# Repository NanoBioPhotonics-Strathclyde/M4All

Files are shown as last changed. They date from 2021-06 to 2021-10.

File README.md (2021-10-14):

# M4All: MultiModal Modular Microscopy for All


M4All is a modular 3D printable microscopy system which allows users to design setups for different imaging modalities (can also be used for non-imaging optical systems). The project is led by Gemma Cairns as part of her PhD in the NanoBioPhotonics group at the University of Strathclyde. Other significant contributers from the group are Brian Patton and past member Stephen Grant.

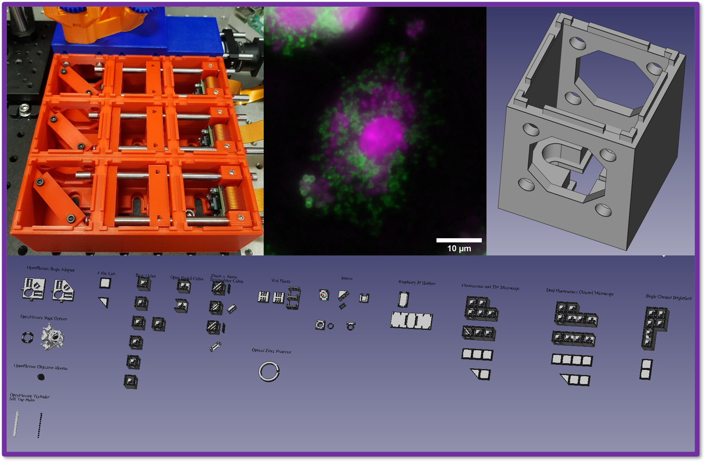
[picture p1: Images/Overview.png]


There are multiple approaches for open microscopy hardware, for example see the project list at https://github.com/HohlbeinLab/OpenMicroscopy, and we recommend trying a few and choosing a project based on what your aims are. When designing this system we approached it from the view point of requiring light tight and stable setups which would allow us to implement and test cutting edge microscopy techniques on a budget. As such M4All is best suited to those with prior microscopy experience or those working with people with similar optical experience. We are confident that M4All systems allow us to generate publication quality images and results.

M4All is based on modular cubes which include 6mm rod holes compatible with standard 30mm cage system optomechanics (multiple manufacturers make compatible components). There are various challenges when it comes to 3D printing, especially when the aim is to create accurate structures for imaging devices. There are often discrepancies between different 3D printers and their printing tolerances. Even small defects in printed parts can be enough to cause problems when trying to join different parts together, which in turn can lead to alignment and stability problems in 3D printed imaging systems. To try and address this problem, our approach is to provide a package of modular cube design files which can be joined together to create larger parts prior to printing to improve stability. By printing larger parts, or ideally the microscope as one single body if printing dimensions allow, this reduces the number of errors that can build up when printing individual modular cubes, although at the expense of decreased flexibility post printing. Note that this approach should not change the total printing time.

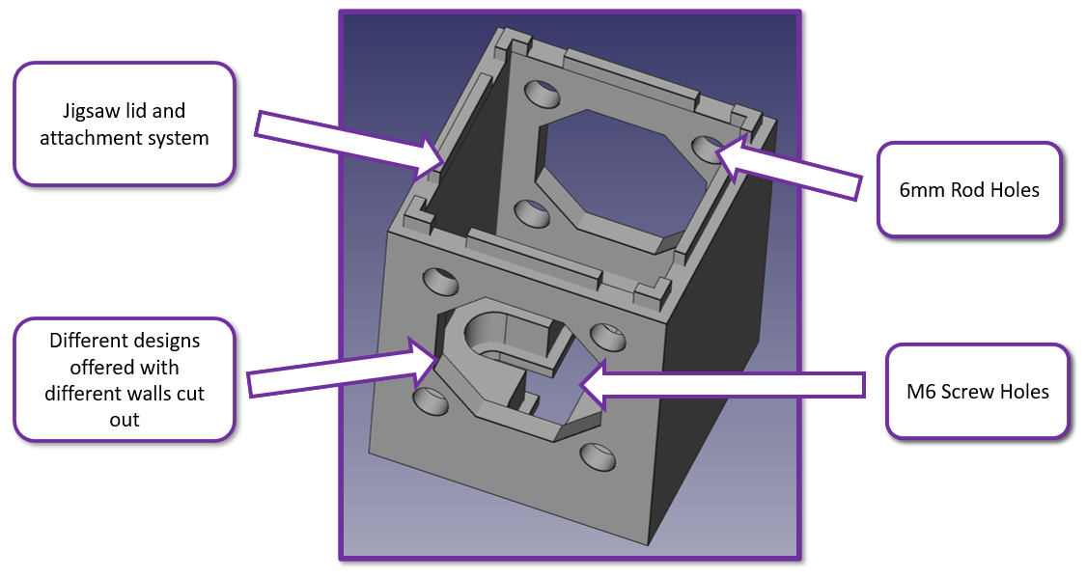
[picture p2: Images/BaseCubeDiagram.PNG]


You can see the base cube design above with the cage system highlighted. The cubes also have M6 screw holes on the bottom to allow securing parts onto an optical bench or other surface and to hold larger parts together in the system. We have included a jigsaw system on the top of the cubes as well to attach corresponding light tight lids or attachments for other parts, such as one we have designed to allow the OpenFlexure Microscope (https://openflexure.org/projects/microscope/) to be compatible with our system. On the topic of keeping imaging systems light tight, we have also provided an array of base cube designs with different walls cut out and including the cage system so that users can design their microscope with the outer walls closed. For alternatives to commercial optomechanics we have also provided designs for 3D printed parts compatible with this system to hold various different optics, such as lenses, mirrors, beamsplitters, dichroics and raspberry pi cameras.

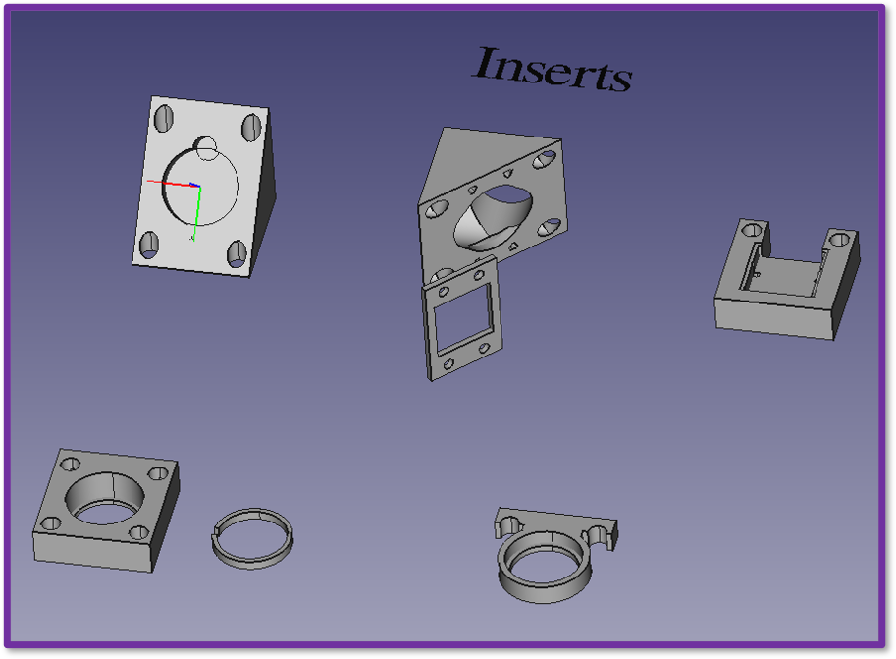
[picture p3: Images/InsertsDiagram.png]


To address the differences in printing tolerances between different 3D printers, we also provide test pieces which users can print to optimise both design dimensions and printer settings. For example the two test pieces shown below allow you to determine which radius to set the 6mm rod holes as in the CAD files so that they aren't too large or small when printing the cubes and inserts. Tolerances also vary for printing in either the xy or z planes and so this is why there are two test piece orientations.

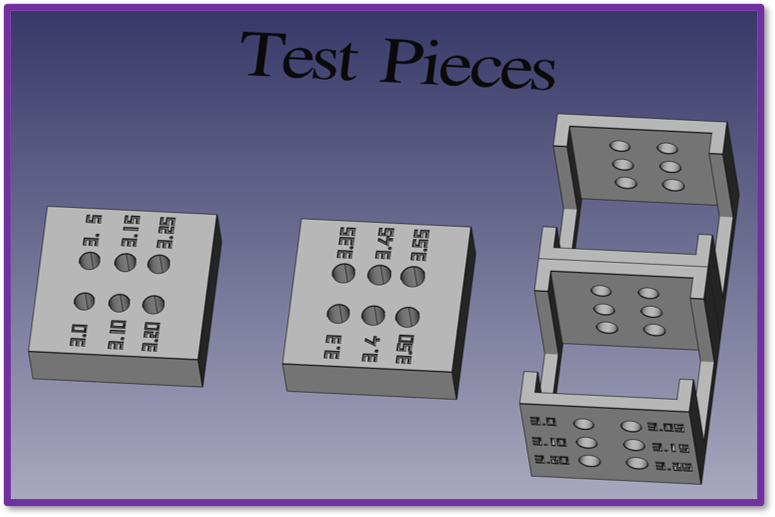
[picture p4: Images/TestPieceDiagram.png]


## Applications

We have used this system to design and build multiple different microscopes.

The first is a [Single Channel Brightfield Microscope](https://github.com/NanoBioPhotonics-Strathclyde/M4All/blob/main/3D%20Printer%20Design%20Files/Build%20Instructions/SingleChannelBrightfield.md). We recommend new users to our system build one of these first to understand our approach and calibrate their 3D printer for our designs.

The next is a [Fluorescence and TIE Microscope](https://github.com/NanoBioPhotonics-Strathclyde/M4All/blob/main/3D%20Printer%20Design%20Files/Build%20Instructions/FluorescenceandTIEMicroscope.md) which shows the level of complexity that can be successfully implemented with our designs:

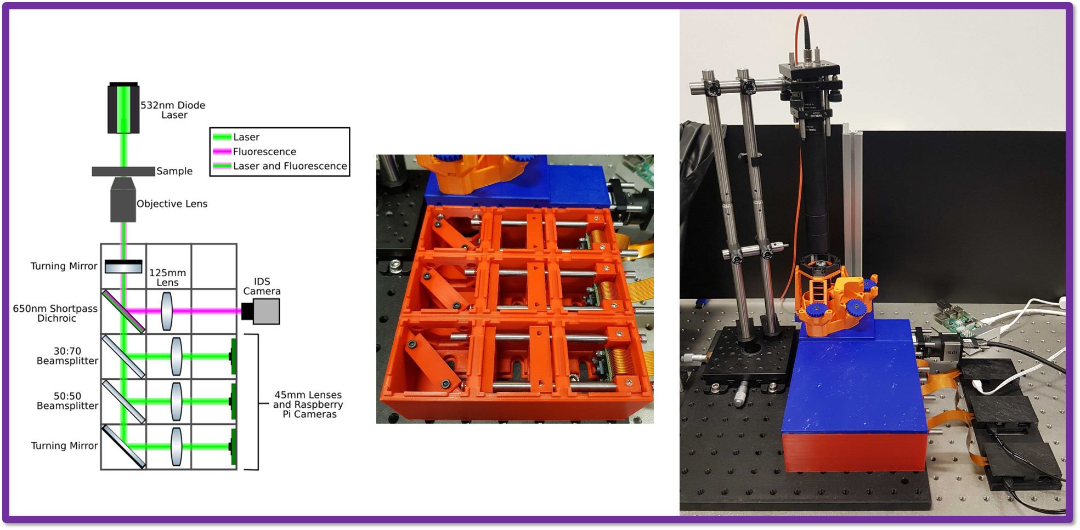
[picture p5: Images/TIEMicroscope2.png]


The third is a [Dual Fluorescence Channel Microscope](https://github.com/NanoBioPhotonics-Strathclyde/M4All/blob/main/3D%20Printer%20Design%20Files/Build%20Instructions/DualFluorescenceMicroscope.md). This microscope takes fluorescence images with the latest Raspberry Pi HQ cameras.

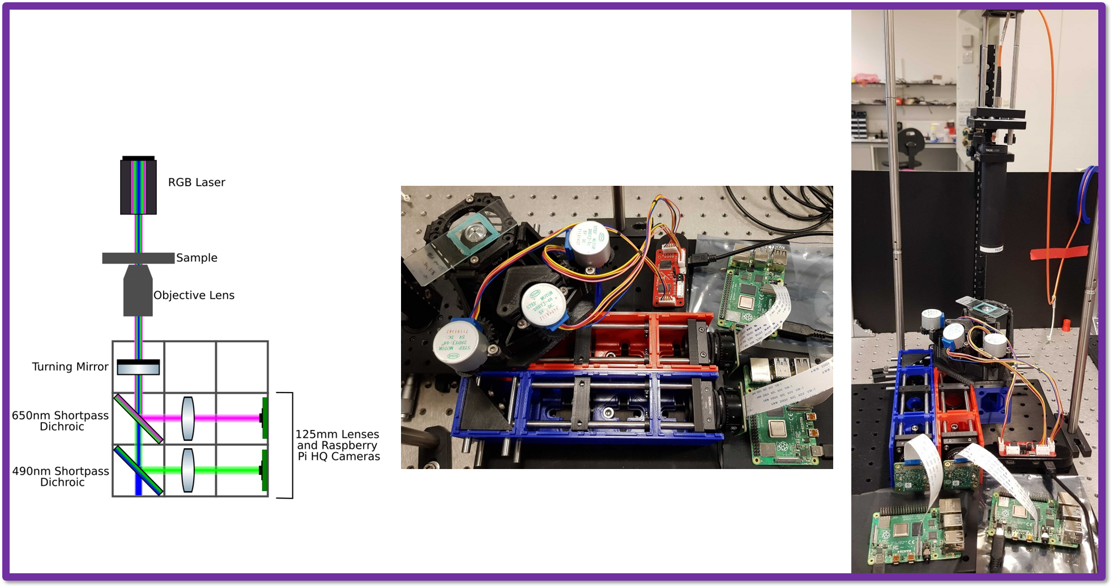
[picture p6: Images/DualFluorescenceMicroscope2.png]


We have successfully used this microscope in a research project to acquire images of bacteria and mitochondria in human monocyte derived macrophages:

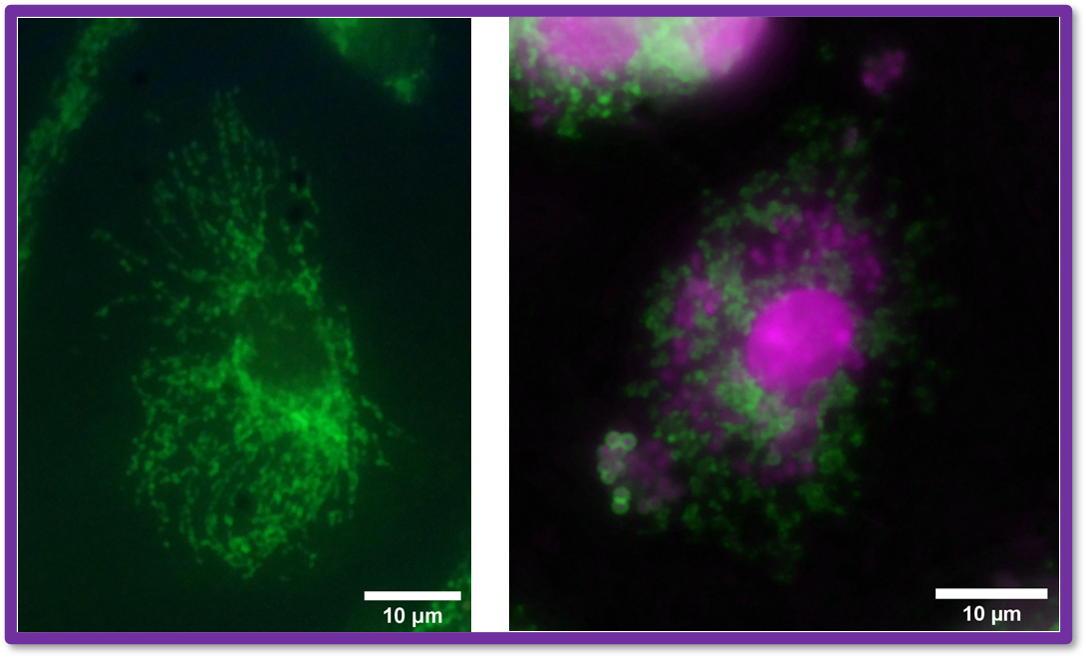
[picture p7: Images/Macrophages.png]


## Design Files and Build Instructions

All of our designs are produced using the open source CAD software FreeCAD (https://www.freecadweb.org/).

Note: We used FreeCAD version 0.18 which can be found here https://github.com/FreeCAD/FreeCAD/releases if there are any compatibility issues with newer releases.

For FreeCAD and STL design files please see the [3D Printer Design Files](https://github.com/NanoBioPhotonics-Strathclyde/M4All/tree/main/3D%20Printer%20Design%20Files) folder.
This section also includes build instructions.

Note: We have also included modified designs from the OpenFlexure project (https://openflexure.org/projects/microscope/). Original designs and modifications are detailed in the design folders in accordance with the CERN Open Hardware Licence.

## Control Software

For microscope control software please see [Control Software](https://github.com/NanoBioPhotonics-Strathclyde/M4All/tree/main/Control%20Software). 

Note: We are not software engineers and so these options may not necessarily be optimal but for now they let us acquire the data that we need for our research.

## Multi Channel Alignment and Calibration Tools

Coming soon...

## Licence

Our hardware designs are licenced under the CERN Open Hardware Licence Version 2 (CERN-OHL-S).

Our software is licenced under the GNU General Public License v3.0.

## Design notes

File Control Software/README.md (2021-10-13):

# Control Software

There are a couple of different options that we use for controlling our 3D printed microscopes, depending on the system. Note: We are not software engineers and so these options may not necessarily be optimal but for now they let us acquire the data that we need for our research.

## Stepper Motor Control

To control the stepper motors connected to the axis actuators on the OpenFlexure stage we use a PiStep2 Quad Stepper Motor Control Board for Raspberry Pi (https://4tronix.co.uk/blog/?p=1309). This is a hat for the Raspberry Pi GPIO pins and allows up to four stepper motors to directly connect to it. We have tested this with a Pi Zero W, Pi 3 Model B+ and Pi 4 Model B. To control the PiStep2 and the motors we have created a simple Python GUI based on Qt and PyQt5. The code can be found in [StepperMotorGUI](https://github.com/NanoBioPhotonics-Strathclyde/M4All/tree/main/Control%20Software/StepperMotorGUI). To run the GUI, open and run the file start.py on your Raspberry Pi. The GUI should look like this:

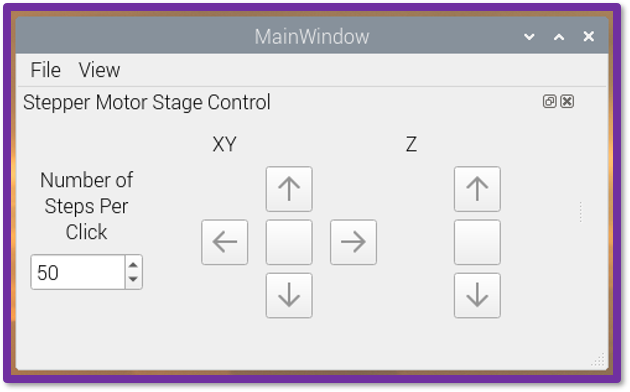
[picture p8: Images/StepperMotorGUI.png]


The default value for the number of steps per click is 50. Altering this will let you control how far the stepper motor turns when you click on the arrow buttons for each axis.

Note: you will need to set up the Pi as outlined [here](https://github.com/NanoBioPhotonics-Strathclyde/M4All/blob/main/Control%20Software/SingleChannelPiSetup.md) for the code to run.

## Single Channel Brightfield Microscope

To see the details of this microscope please go to [Single Channel Brightfield Microscope](https://github.com/NanoBioPhotonics-Strathclyde/M4All/blob/main/3D%20Printer%20Design%20Files/Build%20Instructions/SingleChannelBrightfield.md).

The core components of this microscope are a basic LED for illumination, an OpenFlexure stage, a 60x finite conjugate objective and a Raspberry Pi Camera Module v2. We have created a simple GUI to control this microscope and take timelapse images on the Raspberry Pi camera. The code for this software can be found in [StepperMotorandLEDGUI](https://github.com/NanoBioPhotonics-Strathclyde/M4All/tree/main/Control%20Software/StepperMotorandLEDGUI). Again, to run the GUI, open and run the file start.py on your RaspberryPi. The GUI should look like this:

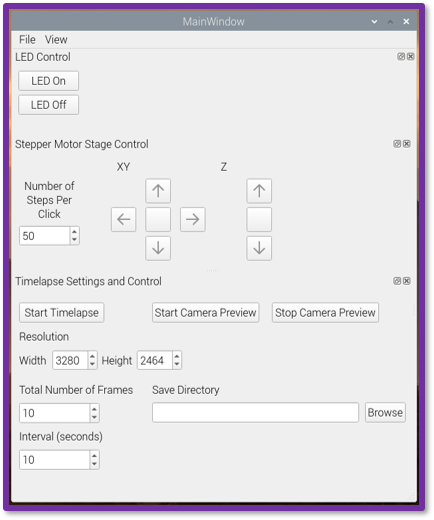
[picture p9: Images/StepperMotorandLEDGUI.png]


This includes control to switch an LED, which is connected to the PiStep2 hat, on and off. Again, please follow the link to the microscope details above for how to connect this. The same stepper motor control as above is included as well as a section to control the Raspberry Pi Camera. A camera preview can be initiated which allows you to view a live feed whilst controlling the stepper motors. When happy with the position, the camera preview must be stopped before starting a timelapse. To start the timelapse, set the desired camera resolution, the total number of frames required and the interval between each frame. Then select a save directory and click start timelapse. When the timelapse is running a camera preview will also be shown.

Note: you will need to set up the Pi as outlined [here](https://github.com/NanoBioPhotonics-Strathclyde/M4All/blob/main/Control%20Software/SingleChannelPiSetup.md) for the code to run.

## Multi Channel Microscopes

Multi channel microscopes using multiple Raspberry Pi cameras, such as our [Fluorescence and TIE Microscope](https://github.com/NanoBioPhotonics-Strathclyde/M4All/blob/main/3D%20Printer%20Design%20Files/Build%20Instructions/FluorescenceandTIEMicroscope.md) and [Fluorescence Channel Microscope](https://github.com/NanoBioPhotonics-Strathclyde/M4All/blob/main/3D%20Printer%20Design%20Files/Build%20Instructions/DualFluorescenceMicroscope.md) require more complex software solutions. This is due to the fact that a Raspberry Pi can only connect to and control a single Raspberry Pi camera module. Because of this, if you want to use multiple Pi cameras, you need to use and control multiple Pi's.

Our current method of choice is to use a Raspberry Pi 4 Model B 8gb as a client (controller) Pi. We then connect each camera and the stepper motor hat to separate Pi's (servers) as can be seen in the microscope links above. We connect the client and server Pi's all to the same network. Instructions for connecting to a network can be found here: https://projects.raspberrypi.org/en/projects/raspberry-pi-using/3#:~:text=If%20you%20want%20to%20connect,connect%20to%20a%20wireless%20network.

To view the camera previews and control the stepper motors we use VNC (Virtual Network Computing) to remote access the server Pi desktops on the client Pi, so that only the client pi needs to be connected to a monitor, mouse and keyboard. For example in the image below you can see one remote desktop on the client Pi has one of the camera previews and the other has the stepper motor control GUI. You can open multiple remote desktops at once and so can have all the camera previews open. If using v2 camera modules, Pi Zero Ws work for the server Pi's, if using HQ camera modules we recommend using at least Pi 3B+ or optimally Pi 4 8GB. 

To set these Raspberry Pi's up please follow the instructions [here](https://github.com/NanoBioPhotonics-Strathclyde/M4All/blob/main/Control%20Software/MultiChannelSetup.md).

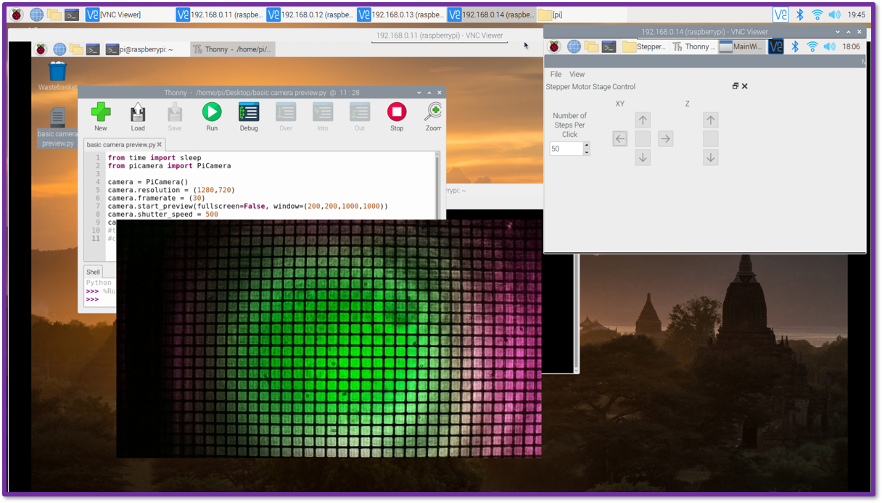
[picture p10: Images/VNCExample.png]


Using the remote desktop approach above, you can capture images from individual cameras using Raspicam (https://www.raspberrypi.com/documentation/accessories/camera.html#raspicam-commands) or Picamera (https://picamera.readthedocs.io/en/release-1.13/). This will save images to the individual pi's that the cameras are connected to and you cannot take images simultaneously.

If you would like to capture images "simultaneously" and save the images to the client Pi then the solution we have been using is the Compound Pi project (https://compoundpi.readthedocs.io/en/release-0.4/). Because the Raspberry Pi cameras use a rolling shutter to capture images there is a limitation on how simultaneous capture can actually be along with any possible network delay using the Compound Pi method. However we have achieved simultaneous capture within one tenth of a second using this method (may be more accurate than this but our stopclock at the time had limited precision). Instructions for setting up the Pi's to use Compound Pi can be found [here](https://github.com/NanoBioPhotonics-Strathclyde/M4All/blob/main/Control%20Software/MultiChannelSimultaneousSetup.md).

Another option separate from using VNC and Compound Pi is to use motionEyeOS (https://github.com/ccrisan/motioneyeos/wiki), however there are limitations on camera resolution and what camera settings you can control.

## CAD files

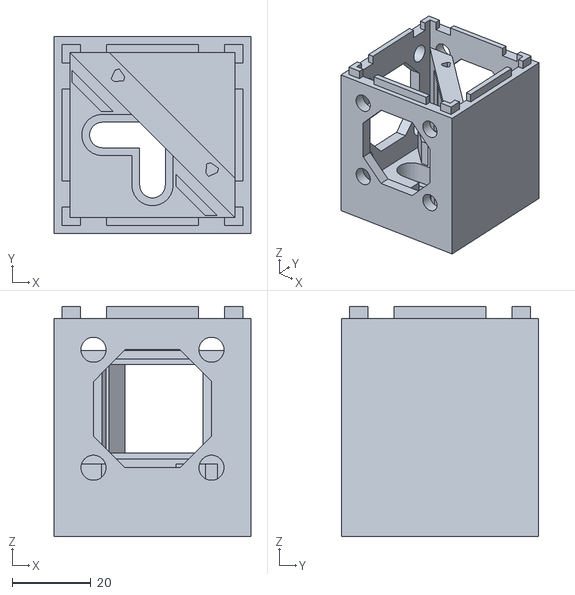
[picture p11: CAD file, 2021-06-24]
3D Printer Design Files/STL Files/25mm x 36mm Beamsplitter Cubes/Beamsplitter Cube 001/Beamsplitter Cube 001.stl
50.0 x 50.0 x 58.5

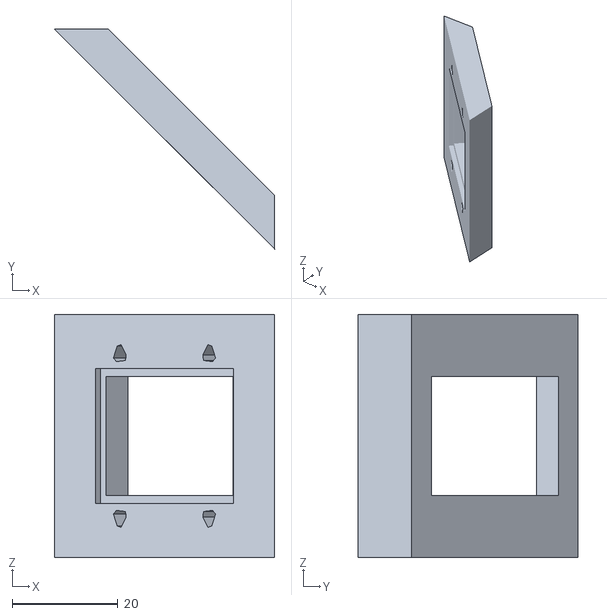
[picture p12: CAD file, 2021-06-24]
3D Printer Design Files/STL Files/25mm x 36mm Beamsplitter Cubes/Beamsplitter Cube 002/Plate Holder.stl
41.7 x 41.7 x 46.0

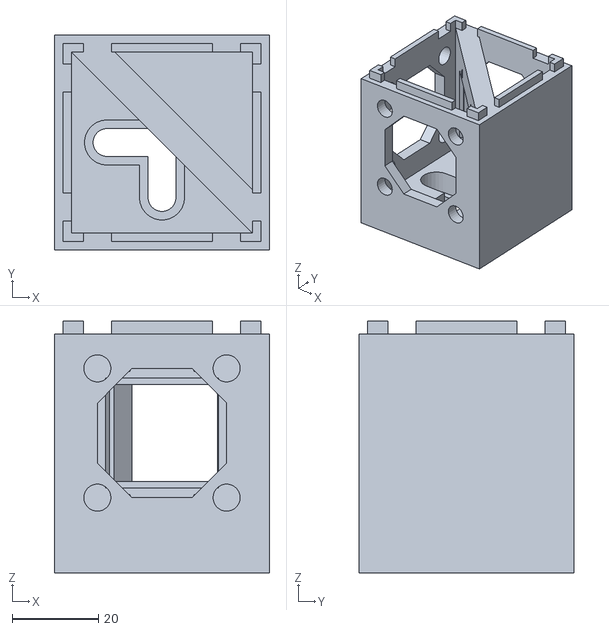
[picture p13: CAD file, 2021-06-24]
3D Printer Design Files/STL Files/25mm x 36mm Beamsplitter Cubes/Beamsplitter Cube/Beamsplitter Cube.stl
50.0 x 50.0 x 58.5

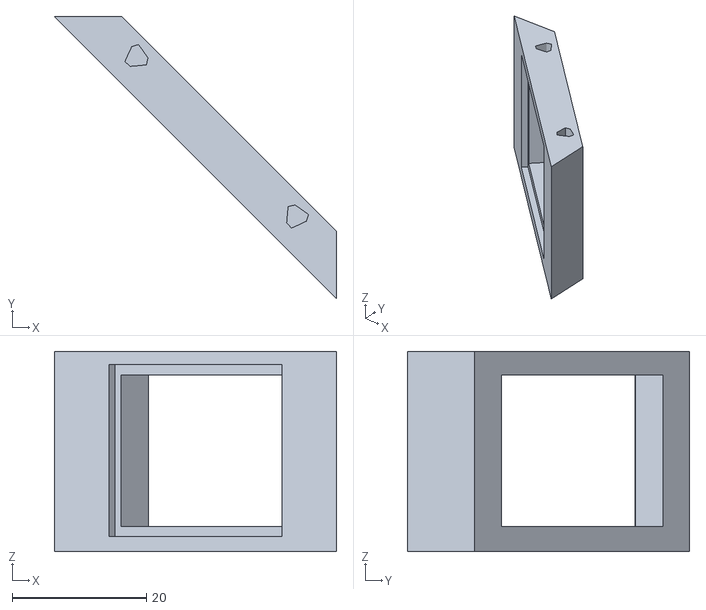
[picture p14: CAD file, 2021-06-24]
3D Printer Design Files/STL Files/25mm x 36mm Beamsplitter Cubes/Plate Holder.stl
42.0 x 42.0 x 29.9

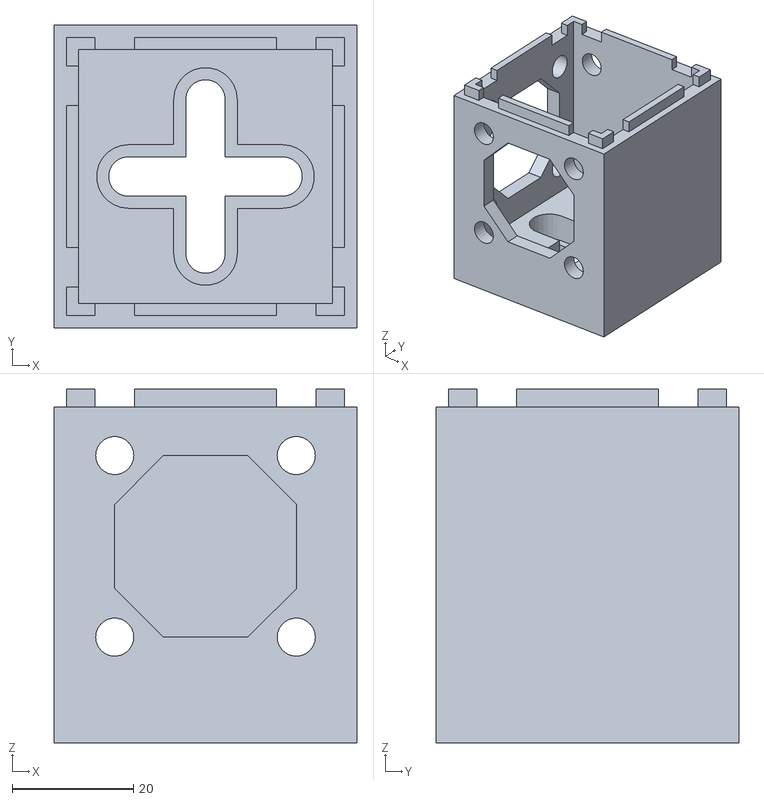
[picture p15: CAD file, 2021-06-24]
3D Printer Design Files/STL Files/Basic Cubes/Cube 2 Sides Cut Out Adjacent.stl
50.0 x 50.0 x 58.5

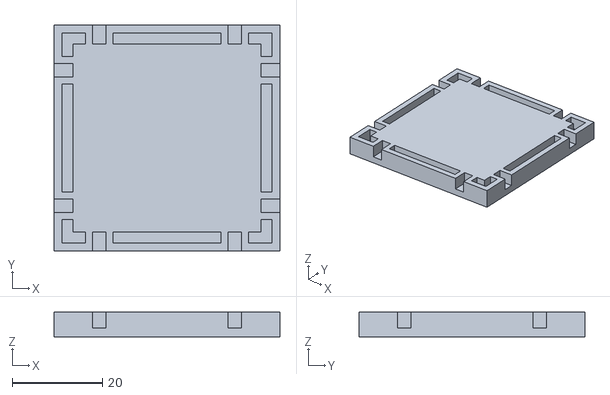
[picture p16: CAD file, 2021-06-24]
3D Printer Design Files/STL Files/Cube Lids/1x1 Cube Lid.stl
50.0 x 50.0 x 5.50

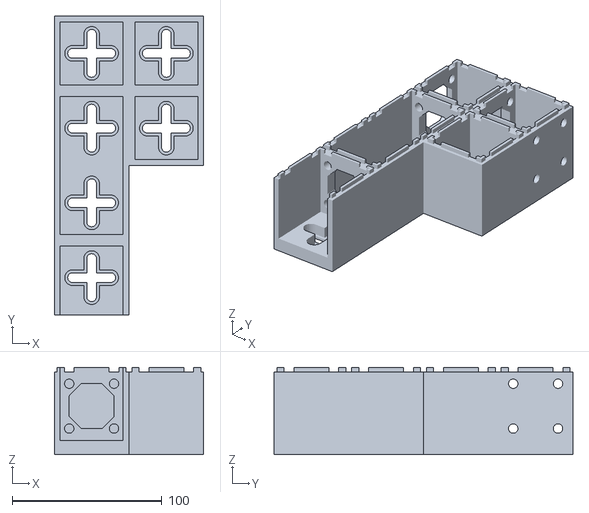
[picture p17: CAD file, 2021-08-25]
3D Printer Design Files/STL Files/Dual Fluorescence Channel Microscope/Channel 1.stl
100.0 x 200.0 x 58.5

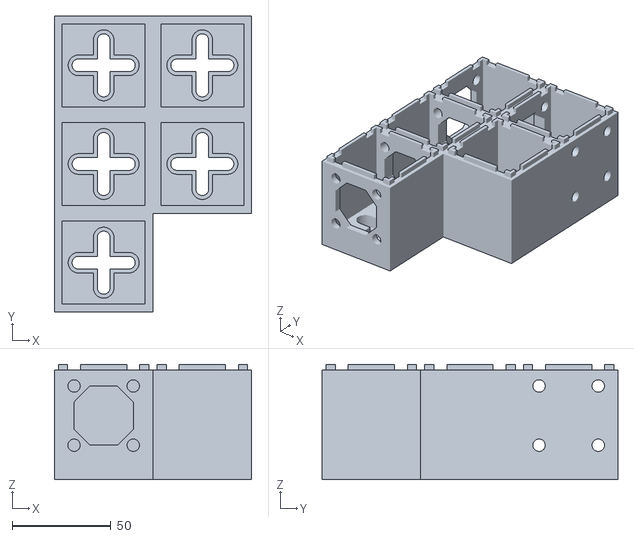
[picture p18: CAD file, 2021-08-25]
3D Printer Design Files/STL Files/Fluorescence and TIE Microscope/Fluorescence Branch.stl
100.0 x 150.0 x 58.5

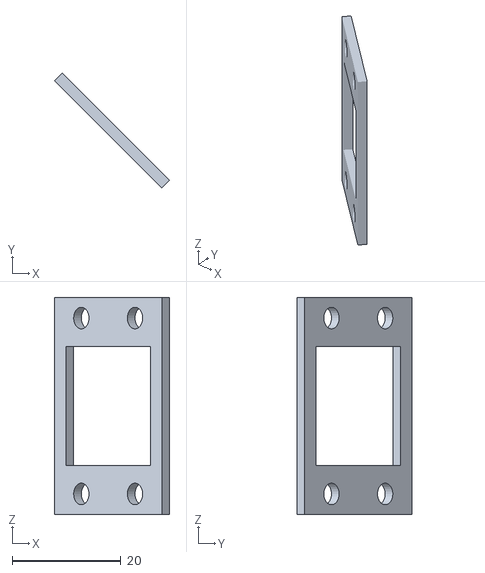
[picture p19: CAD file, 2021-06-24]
3D Printer Design Files/STL Files/Inserts/Dichroic Locker.stl
21.2 x 21.2 x 40.0

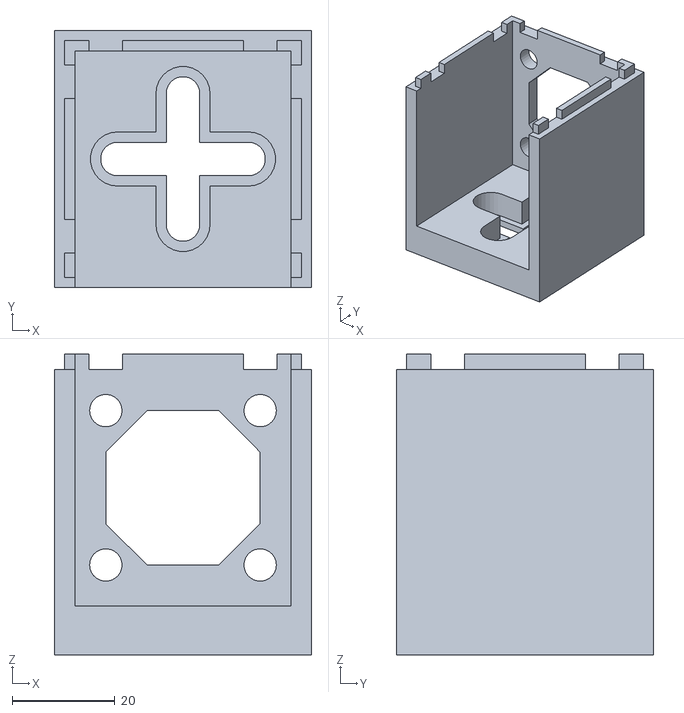
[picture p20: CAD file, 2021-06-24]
3D Printer Design Files/STL Files/Open Ended Cubes/Cube 1 Side Open Ended.stl
50.0 x 50.0 x 58.5

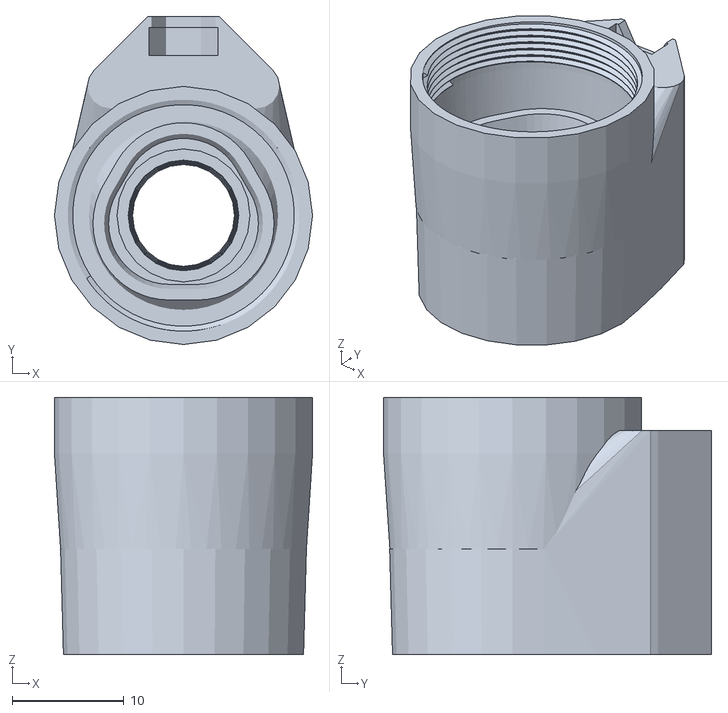
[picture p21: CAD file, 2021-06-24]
3D Printer Design Files/STL Files/OpenFlexure Objective Mount/RMS Objective Mount.stl
23.1 x 29.3 x 23.0

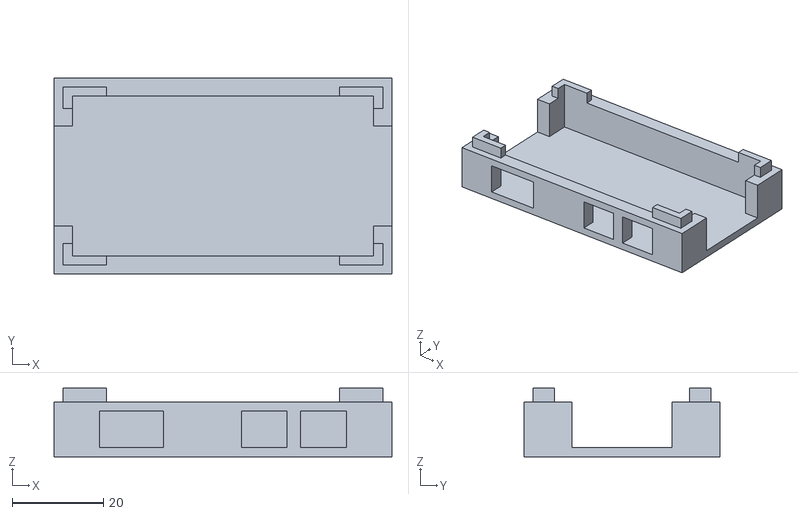
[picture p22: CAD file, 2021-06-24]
3D Printer Design Files/STL Files/Raspberry Pi Holders/Raspberry Pi Zero Case.stl
74.0 x 43.0 x 15.0

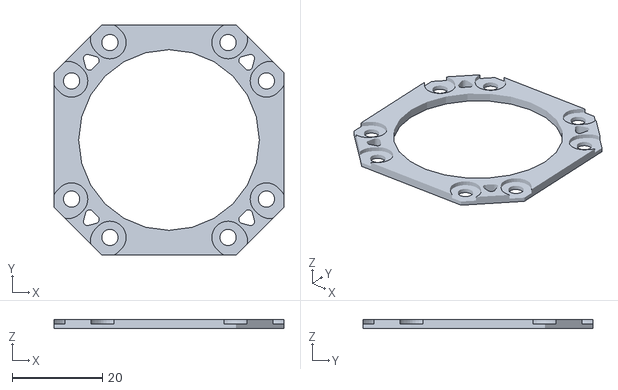
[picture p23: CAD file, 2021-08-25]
3D Printer Design Files/STL Files/Single Channel Brightfield/OpenFlexure Sample Riser Shortened.stl
50.9 x 50.9 x 2.00

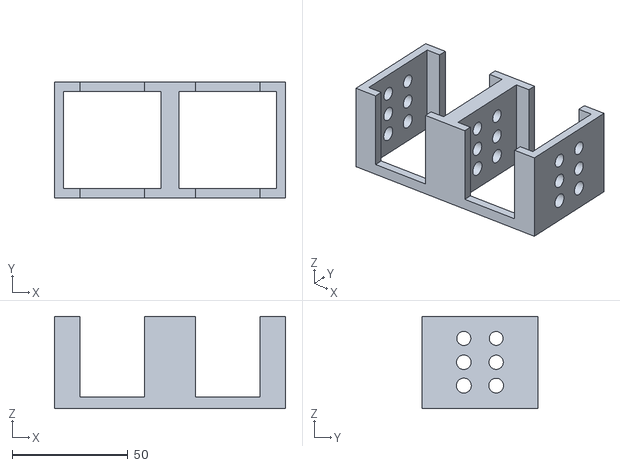
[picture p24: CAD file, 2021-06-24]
3D Printer Design Files/STL Files/Test Pieces/Rod Hole Test Piece Vertical.stl
100.0 x 50.0 x 40.0

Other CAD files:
3D Printer Design Files/STL Files/25mm x 36mm Beamsplitter Cubes/Beamsplitter Cube 002/Beamsplitter Cube 002.stl
3D Printer Design Files/STL Files/25mm x 36mm Beamsplitter Cubes/Beamsplitter Cube/Plate Locker.stl
3D Printer Design Files/STL Files/Basic Cubes/Cube 3 Sides Cut Out.stl
3D Printer Design Files/STL Files/Dual Fluorescence Channel Microscope/OpenFlexure Stage Adapter Corner Cut Out.stl
3D Printer Design Files/STL Files/25mm x 36mm Beamsplitter Cubes/Beamsplitter Cube 002/Plate Locker.stl
3D Printer Design Files/STL Files/Basic Cubes/Cube 0 Sides Cut Out.stl
3D Printer Design Files/STL Files/Basic Cubes/Cube 1 Side Cut Out With Camera Cable Slot.stl
3D Printer Design Files/STL Files/Basic Cubes/Cube 1 Side Cut Out.stl
3D Printer Design Files/STL Files/Basic Cubes/Cube 2 Sides Cut Out.stl
3D Printer Design Files/STL Files/Basic Cubes/Cube 4 Sides Cut Out.stl
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

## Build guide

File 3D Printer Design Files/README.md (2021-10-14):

# Build Instructions

Original FreeCAD design files are in the [FreeCAD Files](https://github.com/NanoBioPhotonics-Strathclyde/M4All/tree/main/3D%20Printer%20Design%20Files/FreeCAD%20Files) folder.

Note: We used FreeCAD version 0.18 which can be found here https://github.com/FreeCAD/FreeCAD/releases if there are any compatibility issues with newer releases.

STL files for 3D printing can be found in the [STL Files](https://github.com/NanoBioPhotonics-Strathclyde/M4All/tree/main/3D%20Printer%20Design%20Files/STL%20Files) folder.

## FreeCAD Instructions

Upon opening the FreeCAD file named "Designs", found [here](https://github.com/NanoBioPhotonics-Strathclyde/M4All/tree/main/3D%20Printer%20Design%20Files/FreeCAD%20Files), you will see that the designs are all grouped into different areas. Below is a brief overview of our design groups with further information found in [Build Instructions](https://github.com/NanoBioPhotonics-Strathclyde/M4All/tree/main/3D%20Printer%20Design%20Files/Build%20Instructions)). Each section in the build instructions has print settings recommended for each part and we also include details of three different microscopes we have built using the M4All system.

Once you have familiarised yourself with our designs we recommend following steps 1 and 2 below to optimise designs/calibrate print settings. We recommend optimising a single cube before printing larger systems. Once happy with this you can either print the parts for one of the three microscopes we describe below (we recommend starting with the single channel brightfield microscope), or you can create your own cube systems using the instructions in step 3 below.

* [**Cubes**](https://github.com/NanoBioPhotonics-Strathclyde/M4All/blob/main/3D%20Printer%20Design%20Files/Build%20Instructions/Cubes.md):
  * **Basic Cubes** are the basic building blocks of the modular system. Included are various cube designs with different numbers of sides cut out for joining together in different orientations for the optical system that the user requires. The cubes have screw holes in the bottom to allow them to be screwed onto an optical table, using M6 screws, for stability and to lock separate parts together. The cubes have 6mm rod holes compatible with 30mm cage system optomechanics.
  * **Open Ended Cubes** are similar to the basic cubes but have entire walls cut out for creating extended cubes where maybe a wall would be at a position where you would like an optical element to be placed. 
  * **25mm x 36mm Beamsplitter Cubes** include three different options for specifically holding 25mm x 36mm plate beamsplitters/dichroics/ mirrors.
  * **Cube Lids** are screwless lids that fix onto the top of the cubes using a jigsaw system to allow a light tight optical setup.
* [**Inserts**](https://github.com/NanoBioPhotonics-Strathclyde/M4All/blob/main/3D%20Printer%20Design%20Files/Build%20Instructions/Inserts.md) includes design files for holding different optical elements using the 30mm cage system. So far these include:
  * a 45 degree 1 inch mirror holder
  * a 1 inch plate dichroic holder with plate to lock dichoic in place.
  * a 1 inch lens holder with retaining ring
  * a Raspberry Pi Camera v2 holder
  * a drop in 1 inch filter holder
* [**Raspberry Pi Holders**](https://github.com/NanoBioPhotonics-Strathclyde/M4All/blob/main/3D%20Printer%20Design%20Files/Build%20Instructions/RaspberryPiHolders.md) includes raspberry pi cases that can be screwed onto an optical table for stability.
* [**OpenFlexure Stage Adapter**](https://github.com/NanoBioPhotonics-Strathclyde/M4All/blob/main/3D%20Printer%20Design%20Files/Build%20Instructions/OpenFlexureStageAdapter.md) is an adapter plate for the OpenFlexure microscope, using the same jigsaw system as the cube lids, to allow the OpenFlexure xyz stage to be used.
* **Test Pieces** allow users to find the best settings and design dimensions for their specific 3D printers before printing full designs.
* [**Single Channel Brightfield Microscope**](https://github.com/NanoBioPhotonics-Strathclyde/M4All/blob/main/3D%20Printer%20Design%20Files/Build%20Instructions/SingleChannelBrightfield.md) includes larger parts recommended to build a simple single channel brightfield microscope. We recommend building one of these first if new to our system in order to understand our approach and calibrate your 3D printer for our designs.
* [**Fluorescence and TIE Microscope**](https://github.com/NanoBioPhotonics-Strathclyde/M4All/blob/main/3D%20Printer%20Design%20Files/Build%20Instructions/FluorescenceandTIEMicroscope.md) includes larger recommended parts made up of the modular cubes for a multimodal microscope setup including fluorescence and computational phase contrast imaging.
* [**Dual Fluorescence Channel Microscope**](https://github.com/NanoBioPhotonics-Strathclyde/M4All/blob/main/3D%20Printer%20Design%20Files/Build%20Instructions/DualFluorescenceMicroscope.md) again includes larger recommended parts for a dual channel fluorescence microscope.

### Step 1: Test Pieces

As the tolerances of different models of 3D printers and different 3D printing materials vary, it is recommended to print the test parts provided [here](https://github.com/NanoBioPhotonics-Strathclyde/M4All/tree/main/3D%20Printer%20Design%20Files/STL%20Files/Test%20Pieces) to optimise print settings and design dimensions. Tolerances also vary for printing in either the xy or z planes and so this is why there are two test piece orientations.

1. **Rod Hole Test Piece Vertical** allows users to test what rod hole radius to use for the cube walls and any inserts or parts where the print orientation means the rod hole is on a vertical wall. The test piece includes rod hole radii ranging from 3-3.25mm. Three vertical walls are included in the test piece so users can check the 6mm metal rods go through multiple walls. Note: you want there to be enough friction that the rods don't slide about but not too much friction so that the rods can't easily go through multiple walls.
2. **Rod Hole Test Piece Horizontal** includes two test pieces for testing what rod hole radius to use for any inserts or parts where the print orientation means the rod hole is on a horizontal wall. They cover radii from 3-3.55mm.

The user can test these parts with different print settings, such as varying layer height and infill, for optimisation.

We don't currently have test pieces for optimising inserts. However in the build instructions we detail how to alter important dimensions in case you need to change these for your printer or optics. We suggest starting off with the recommended print settings and adjusting appropriately there after.

### Step 2: Altering Design Dimensions Based on Test Pieces

Once you have determined what rod hole radius to use based on the test pieces, you can then alter the FreeCAD designs accordingly, if needed.

FreeCAD is a parametric 3D CAD modeler, meaning 2D sketches are turned into 3D objects using constraints. Therefore the rod hole sketches can be easily altered by changing the radius constraint in the 2D sketch as shown below.

1. Select the necessary body from the tree view and expand. 
2. Find the rod hole sketches. There will be one for each cube wall.
3. Open up the sketch.
4. Alter the radius contraints to the required value.

Note: Currently this needs to be done manually for all sketches and bodies/parts.



### Step 3: Joining Cube Designs Together

The modularity of the M4All system comes from modular design files which can be joined together before printing to create stable larger parts. Each 50x50mm cube has M6 screw holes on the bottom for fixing to an optical table, jigsaw lid system and 6mm metal rod holes for a 30mm cage system. By joining different cube designs together, users can create suitable parts for their optical systems. The clip below shows how to join two cubes together. 

1. From the tree menu on the left hand side, duplicate the required cubes (FreeCAD Body) using Ctrl+C and Ctrl+V either into the same FreeCad file or a new file. The duplicates will be in the same position as the original bodies.
2. To move the position of the cubes, click on the body in the tree view and alter the x and y positions. As the cubes are 50x50mm, offsetting them in 50mm increments will allow the walls to be joined with the cut outs and rod holes aligning with each other.
3. If step 3 was done correctly, when you export to an stl file the cubes will be fused together and print as one with no joins evident. 
4. To export to an stl file for 3D printing you can either select the two bodies and go to File>Export and save as a .stl, or you can create a Part in FreeCad and add the two bodies (cubes) to the Part. This is useful if creating a part with many body files. You can then simply select the Part in the tree view and again go to File>Export and save as a .stl file (as in the clip below).

Parts in the "Fluorescence and TIE Microscope" and "Dual Fluorescence Channel Microscope" groups were created using this process.

Individual cube lids can also be joined together in this way to create monolithically printed lids to cover your specific cube designs. 

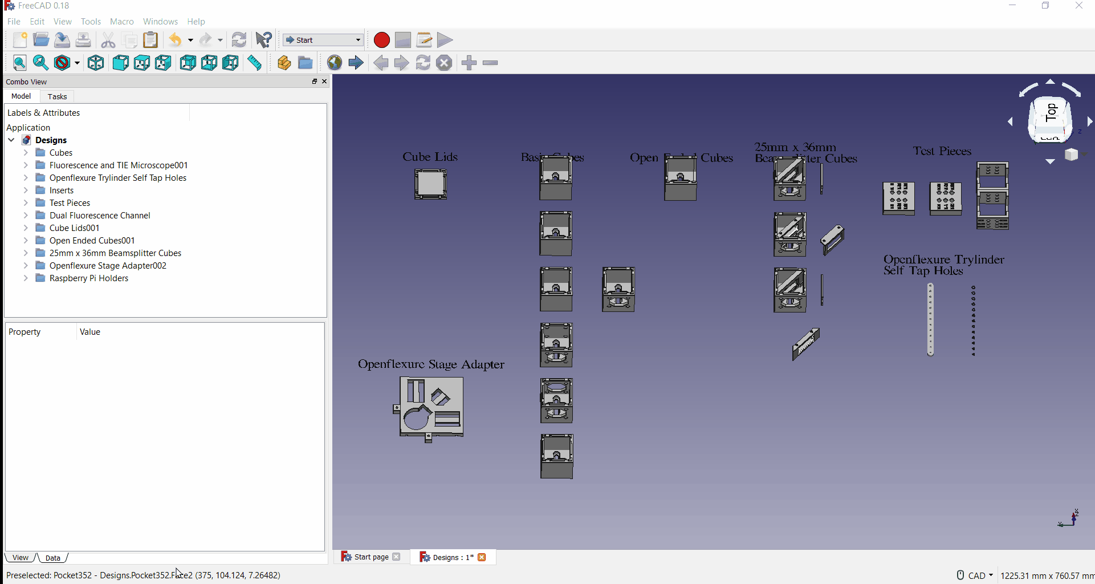
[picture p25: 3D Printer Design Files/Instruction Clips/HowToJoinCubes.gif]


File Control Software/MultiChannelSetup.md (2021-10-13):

# Setting Up VNC to Control Multiple Pi's

## Setting Up the Client

Firstly set up the client Raspberry Pi (recommended to use a Raspberry Pi 4 Model B 8gb), connect to a monitor, keyboard and mouse and install Raspberry Pi OS (32-bit) according to the instructions on the official Raspberry Pi website (https://projects.raspberrypi.org/en/projects/raspberry-pi-setting-up/0).

The OS doesn't use Python 3 by default and so follow the instructions here to use Python 3 and install pip: https://learn.sparkfun.com/tutorials/python-programming-tutorial-getting-started-with-the-raspberry-pi/all

Connect to a network following these instructions: https://projects.raspberrypi.org/en/projects/raspberry-pi-using/3#:~:text=If%20you%20want%20to%20connect,connect%20to%20a%20wireless%20network.

If it's not already installed then download VNC viewer from: https://www.realvnc.com/en/connect/download/viewer/raspberrypi/

## Setting Up the Servers

To do this you can shut down and disconnect the power from the client Pi that you have already connected to a monitor etc. Then you can swap to a fresh SD card to set up a server Pi (keeping the client SD card in a safe place in the mean time). Or you can connect your server Pi to a monitor etc.

Again install Raspberry Pi OS (32-bit) according to the instructions on the official Raspberry Pi website (https://projects.raspberrypi.org/en/projects/raspberry-pi-setting-up/0).

Connect to a network following these instructions: https://projects.raspberrypi.org/en/projects/raspberry-pi-using/3#:~:text=If%20you%20want%20to%20connect,connect%20to%20a%20wireless%20network.

The OS doesn't use Python 3 by default and so follow the instructions here to use Python 3 and install pip: https://learn.sparkfun.com/tutorials/python-programming-tutorial-getting-started-with-the-raspberry-pi/all

Now open a terminal on the Raspberry Pi and install the following:

* PyQt5: sudo apt-get install python3-pyqt5
* qt5-default: sudo apt-get install qt5-default
* qtcreator: sudo apt-get install qtcreator
* OpenCV: pip install opencv-contrib-python

All other packages such as numpy, RPi.GPIO, threading etc. should already be installed with Raspberry Pi OS.

For the server Pi that will be used to control the stage stepper motors also save a copy of the [StepperMotorGUI](https://github.com/NanoBioPhotonics-Strathclyde/M4All/tree/main/Control%20Software/StepperMotorGUI) to the Pi.

To enable VNC follow step 1 here: https://magpi.raspberrypi.com/articles/vnc-raspberry-pi

Then open up VNC server, go to Options > Troubleshooting and check "Enable direct capture mode" and apply and click ok.

Also when you open VNC server note down the IP address that has been assigned to the Pi to use in VNC viewer. Or you also have the option to set a static IP address. To do this edit the dhcpcd file by typing sudo nano /etc/dhcpcd.conf into the terminal. Go down to the bottom and uncomment the below lines and change them to:
	
interface wlan0

static ip_address=192.168.0.10/24 

static routers=192.168.0.1

static domain_name_servers=192.168.0.1

For the static ip_address above you can set different server Pi's to 192.168.0.11/24, 192.168.0.12/24, 192.168.0.13/24 etc.

You can either repeat this process for all the server Pi SD cards or you can clone one that has already been set up via this [method](https://www.howtogeek.com/341944/how-to-clone-your-raspberry-pi-sd-card-for-foolproof-backup/). However, you will then need to find all their IP addresses for example using an IP scanner https://learn.pimoroni.com/article/finding-your-raspberry-pi or after cloning manually changing their static IP address.

Once all the SD cards are set up then they can be inserted into the relevant Pi's connected to a camera or stepper motor hat and the client SD card can be inserted back into the client Pi. Upon powering on all the Pi's they should connect automatically to the network which was selected during set up.

If VNC viewer on the client Pi cannot connect to a certain IP address then it may be that the server hasn't in fact conected to the network upon boot. If this happens, which we have come across when using a Pi 4 as a server, then follow the below instructions:

Plug the server SD card into a windows computer. To the boot partition create a blank file using notebook and save it as ssh. Don't save it with a file extension. Then also create a file called wpa_supplicant.conf with the following wifi network info (changing the ssid and psk to your network info):

country=GB

ctrl_interface=DIR=/var/run/wpa_supplicant GROUP=netdev

update_config=1

network={

    ssid="NETWORK-NAME"
    
    psk="NETWORK-PASSWORD"
    
}

Once done, replace the SD card back into the server pi and boot.

Then on your controller pi which is connected to the same network open a terminal and type in:

ssh pi@192.168.0.10

Replace the IP address above with whatever the IP address for the server Pi is.

Then you can put in the password and the pi should boot.

Now you should be able to open the pi using vnc viewer.

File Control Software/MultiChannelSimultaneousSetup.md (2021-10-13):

# Setting Up Compound Pi to Control Multiple Pi's

## Setting Up the Client

Firstly set up the client Raspberry Pi (recommended to use a Raspberry Pi 4 Model B 8gb), connect to a monitor, keyboard and mouse and install Raspberry Pi OS (32-bit) according to the instructions on the official Raspberry Pi website (https://projects.raspberrypi.org/en/projects/raspberry-pi-setting-up/0).

Connect to a network following these instructions: https://projects.raspberrypi.org/en/projects/raspberry-pi-using/3#:~:text=If%20you%20want%20to%20connect,connect%20to%20a%20wireless%20network.

If it's not already installed then download VNC viewer from: https://www.realvnc.com/en/connect/download/viewer/raspberrypi/

Open a terminal and install the following:

* sudo apt-get update
* sudo apt-get install compoundpi-client ntp

Reboot the Pi.

Set a static IP address. To do this edit the dhcpcd file by typing sudo nano /etc/dhcpcd.conf into the terminal. Go down to the bottom and uncomment the below lines and change them to:
	
interface wlan0

static ip_address=192.168.0.10/24 

static routers=192.168.0.1

static domain_name_servers=192.168.0.1

Reboot the Pi.

## Setting Up the Servers

Note: these instructions are only for server Pi's connected to cameras. For the server connected to the stepper motors please follow the server setup [here](https://github.com/NanoBioPhotonics-Strathclyde/M4All/blob/main/Control%20Software/MultiChannelSetup.md).

You can shut down and disconnect the power from the client Pi that you have already connected to a monitor etc. Then you can swap to a fresh SD card to set up a server Pi (keeping the client SD card in a safe place in the mean time). Or you can connect your server Pi to a monitor etc.

Again install Raspberry Pi OS (32-bit) according to the instructions on the official Raspberry Pi website (https://projects.raspberrypi.org/en/projects/raspberry-pi-setting-up/0).

Connect to a network following these instructions: https://projects.raspberrypi.org/en/projects/raspberry-pi-using/3#:~:text=If%20you%20want%20to%20connect,connect%20to%20a%20wireless%20network.

To enable VNC follow step 1 here: https://magpi.raspberrypi.com/articles/vnc-raspberry-pi

Then open up VNC server, go to Options > Troubleshooting and check "Enable direct capture mode" and apply and click ok.

Open a terminal and install:

* sudo apt-get install compoundpi-server ntp

Set a static IP address. To do this edit the dhcpcd file by typing sudo nano /etc/dhcpcd.conf into the terminal. Go down to the bottom and uncomment the below lines and change them to:
	
interface wlan0

static ip_address=192.168.0.11/24         (Note: for each Pi change to 192.168.0.12/24, 192.168.0.13/24 etc.)

static routers=192.168.0.1

static domain_name_servers=192.168.0.1

Reboot the Pi.

Edit the /etc/ntp.conf file and replace the server lines with the IP address of your client:

...

#server 0.debian.pool.ntp.org iburst

#server 1.debian.pool.ntp.org iburst

#server 2.debian.pool.ntp.org iburst

#server 3.debian.pool.ntp.org iburst

server 192.168.1.2

...

Restart the NTP daemon:

* sudo service ntp restart

Reboot the Pi.

## Using Compound Pi and VNC

Compound Pi allows the simultaneous capture (within limits) of images from different Raspberry Pi cameras connected to different Raspberry Pi's. However, it does not offer a method of previewing the camera streams before. Therefore, we use this in combination with remote desktops through VNC to preview cameras. With all of the prepared SD cards in their respective Pi's, and the Pi's booted, open the server Pi's on VNC viewer on the client using the static IP addresses that you assigned them. On the remote desktop for each server that you would like to view the camera open a terminal and type in:

* sudo service cpid stop

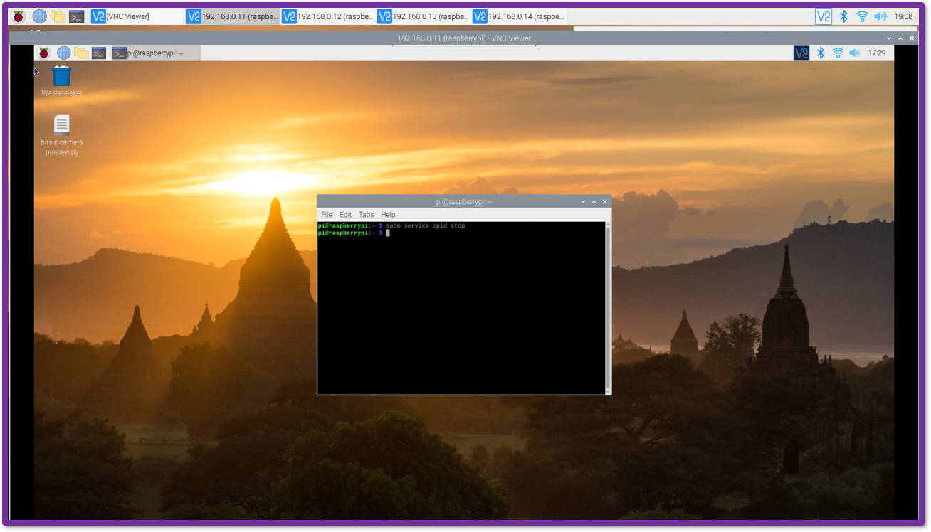
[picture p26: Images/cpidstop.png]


Once you have done this you will be able to either use Raspicam or Picamera to view the camera preview on the remote desktop. This will allow you to get your sample into position and focus etc. Then once you are happy and would like to capture images, open the terminal again and type:

* sudo service cpid start

After this, minimise the remote desktops on the client and open a terminal on the client and type:

* cpi

This will start the compoundpi client.

Then type:

* set network 192.168.0.1/24
* set timeout 400
* find n (where n is the number of server pi's you want to capture from or you can add a specific server by typing add 192.168.0.11 etc.)
* resolution 3280x2462
* framerate 30
* iso 200
* exposure 50
* set output /home/pi/
* capture
* download

You can change the camera settings above and set the output to a folder on the client where you want the images to save to. When you type capture, the servers all capture an image on their Pi camera and then download pulls them over to the client. When you download them it also clears the images from the servers.

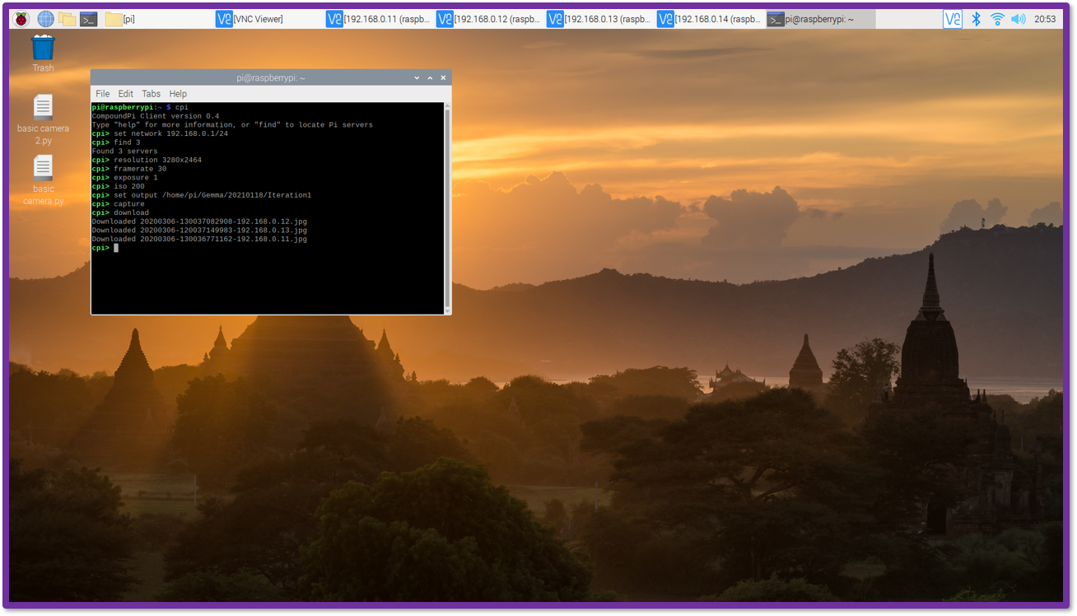
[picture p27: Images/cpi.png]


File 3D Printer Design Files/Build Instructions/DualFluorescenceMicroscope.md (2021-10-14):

# Dual Fluorescence Channel Microscope

This section of the FreeCAD file includes designs where we have placed the individual cube designs together to create larger parts for 3D printing. These designs are specifically for parts for a dual fluorescence channel microscope. The wavelength ranges of the detection channels can be chosen by the user by selecting specific dichroic mirrors. In this case we have chosen a 650nm shortpass dichroic mirror and a 490nm shortpass dichroic mirror to create two detection channels, one which detects fluorescence above 650nm and the other which detects fluorescence between 490nm and 650nm.

Note: we are using the new Raspberry Pi HQ cameras in this microscope to capture fluorescence images. These cameras come with an IR filter on them which means if you are trying to image far red fluorescence, the emission will be blocked by the filter. You can follow the instructions [here](https://www.raspberrypi.com/documentation/accessories/camera.html#raspberry-pi-hq-camera-filter-removal) to remove this filter from the camera if using one of these cameras in this detection window.



We have used this microscope in a research project to image mitochondria and bacteria inside human monocyte derived macrophages (samples made by Katharin Balbirnie-Cumming from the Dockrell group at the Centre for Inflammation Research, University of Edinburgh):



The dual colour image above followed the below processing steps. Image quality will be affected by sample preparation as well as microscope design. As you can see below, the bacteria image had a high background signal which we believe is background labelling and so we have carried out a rolling ball background subtraction for image representation.

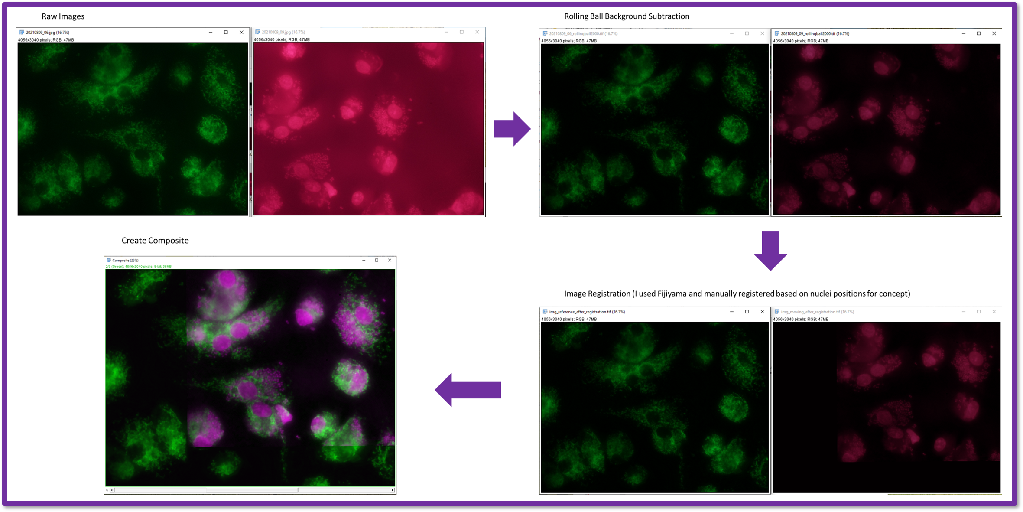
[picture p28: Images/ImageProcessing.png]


## Parts to Print

All the STL files needed for this microscope can be found in [Dual Fluorescence Channel Microscope](https://github.com/NanoBioPhotonics-Strathclyde/M4All/tree/main/3D%20Printer%20Design%20Files/STL%20Files/Dual%20Fluorescence%20Channel%20Microscope).

These are the two main cube parts and lids:

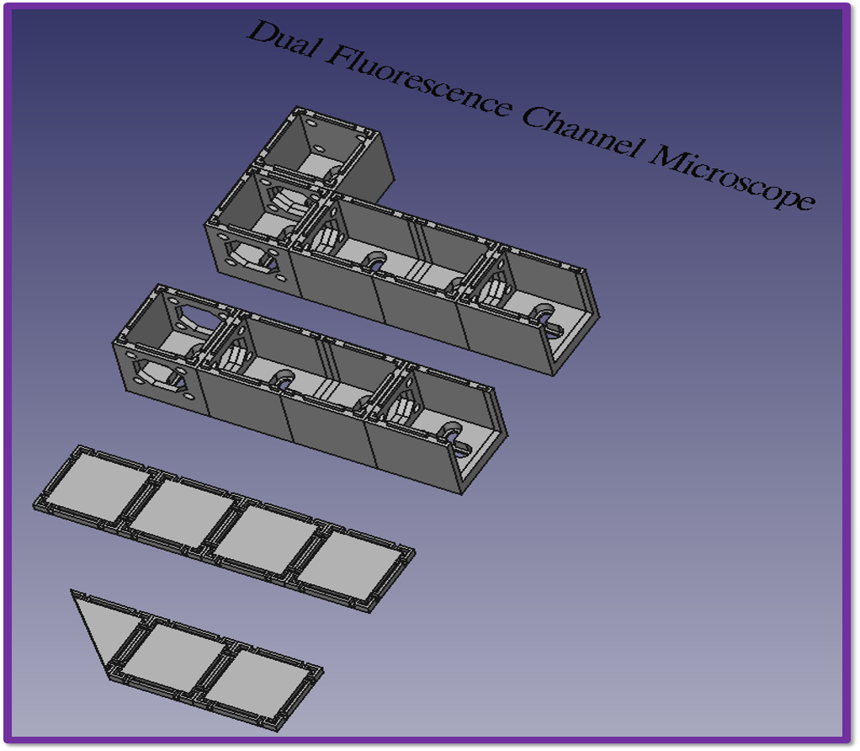
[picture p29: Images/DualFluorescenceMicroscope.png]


STL files to print (print settings can be found in the [Cubes](https://github.com/NanoBioPhotonics-Strathclyde/M4All/blob/main/3D%20Printer%20Design%20Files/Build%20Instructions/Cubes.md) and [Inserts](https://github.com/NanoBioPhotonics-Strathclyde/M4All/blob/main/3D%20Printer%20Design%20Files/Build%20Instructions/Inserts.md) build instructions):

* 2x 1 Inch Dichroic Holder
* 2x 1 Inch Lens Holder
* 2x 1 Inch Retaining Ring
* 1x 45 Degree Mirror Holder
* 1x Channel 1
* 1x Channel 2
* 2x Dichroic Locker
* 2x Drop In Filter Holder
* 1x Fluorescence Channel 1 Lid
* 1x Fluorescence Channel 2 Lid
* 1x OpenFlexure Joined to Objective Mount
* 1x OpenFlexure Sample Riser Shortened
* 1x OpenFlexure Stage Adapter Corner Cut Out

Also from the OpenFlexure [website](https://microscope-stls.openflexure.org/#/v6.1.5?enable_smart_brim=true&reflection_illumination=false&optics=rms_f50d13&camera=picamera_2&use_pilens_optics_module=false&riser=sample&microscope_stand%3Abox_h=30&pi_in_base=true&base=bucket&legacy_picamera_tools=false&include_actuator_tension_band=false&include_actuator_drilling_jig=false&motorised=true&use_motor_gears_for_hand_actuation=false) please print the gears, small gears and sample clips STL files.

## Bill of Materials

* Light source:
  * 1x Compact RGB Laser - World Star Tech COMPACT-TS-40-RGB-FC (https://www.worldstartech.com/wp-content/uploads/2017/03/COMPACT-RGB-1.pdf)
  * 1x Thorlabs M42L05 - Ø50 µm, 0.22 NA, Low OH, FC/PC-FC/PC Fiber Patch Cable, 5 m (https://www.thorlabs.com/thorproduct.cfm?partnumber=M42L05)
  * 1x Thorlabs LB1811-A-ML - Mounted N-BK7 Bi-Convex Lens, Ø1", f = 35.0 mm, ARC: 350-700 nm (https://www.thorlabs.com/thorproduct.cfm?partnumber=LB1811-A-ML) - for focusing light from fibre onto sample)
  * 1x Thorlabs FESH0650 - Ø25.0 mm Premium Shortpass Filter, Cut-Off Wavelength: 650 nm (https://www.thorlabs.com/thorproduct.cfm?partnumber=FESH0650)
* Turning mirror:
  * 1x Thorlabs PF10-03-P01 - Ø1" Protected Silver Mirror (https://www.thorlabs.com/thorproduct.cfm?partnumber=PF10-03-P01)
* Dichroic Mirrors for fluorescence channels:
  * 1x Thorlabs DMSP650 - Ø1" Shortpass Dichroic Mirror, 650 nm Cutoff (https://www.thorlabs.com/thorproduct.cfm?partnumber=DMSP650)
  * 1x Thorlabs DMSP490 - Ø1" Shortpass Dichroic Mirror, 490 nm Cutoff (https://www.thorlabs.com/thorproduct.cfm?partnumber=DMSP490)
* Longpass filters to clean up fluorescence channels:
  * 1x Thorlabs FEL0650 - Ø1" Longpass Filter, Cut-On Wavelength: 650 nm (https://www.thorlabs.com/thorproduct.cfm?partnumber=FEL0650)
  * 1x Thorlabs FEL0500 - Ø1" Longpass Filter, Cut-On Wavelength: 500 nm (https://www.thorlabs.com/thorproduct.cfm?partnumber=FEL0500)
* Tube lenses:
  * 2x Thorlabs AC254-125-A - f = 125 mm, Ø1" Achromatic Doublet, ARC: 400 - 700 nm (https://www.thorlabs.com/thorproduct.cfm?partnumber=AC254-125-A) - Tube lens for Fluorescence Channel
* Cameras:
  * 2x Raspberry Pi High Quality Camera (https://www.raspberrypi.org/products/raspberry-pi-high-quality-camera/)
  * 2x CP33/M - SM1-Threaded 30 mm Cage Plate, 0.35" Thick, 2 Retaining Rings, M4 Tap (https://www.thorlabs.com/thorproduct.cfm?partnumber=CP33/M)
  * 2x Thorlabs SM1A9 - Adapter with External C-Mount Threads and Internal SM1 Threads, 4.4 mm Spacer (https://www.thorlabs.com/thorproduct.cfm?partnumber=SM1A9)
  * 2x Thorlabs SM1T2 - SM1 (1.035"-40) Coupler, External Threads, 0.5" Long, Two Locking Rings (https://www.thorlabs.com/thorproduct.cfm?partnumber=SM1T2)
* Objective:
  * 1x Newport LI-60x Microscope Objective Lens, Infinity Corrected, 60x, 0.85 NA, 0.3 mm WD (https://www.newport.com/p/LI-60X) - This objective has been discontinued, this is Newport's new equivalent: https://www.newport.com/p/LIO-60X
* Cage rods:
  * 12x Thorlabs ER6 - Cage Assembly Rod, 6" Long, Ø6 mm (https://www.thorlabs.com/thorproduct.cfm?partnumber=ER6)
  * An equivalent to the Thorlabs rods is to buy lower cost stainless steel 6mm diameter rods. For example we bought 1.5m long rods from RS Components and cut them down to size - https://uk.rs-online.com/web/p/metal-bars-metal-rods/6614680/
* Electronics:
  * 1x Raspberry Pi Zero W (We recommend getting a starter kit, such as https://uk.rs-online.com/web/p/raspberry-pi/1812039/ so that everything you need is included)
  * 3x Raspberry Pi 4 8gb (Again recommend a starter kit https://uk.rs-online.com/web/p/raspberry-pi/2012367)
  * 1x PiStep2 Quad Stepper Controller for Raspberry Pi (https://4tronix.co.uk/blog/?p=1309)
  * 3x 28BYJ-48 5V DC Stepper Motor (https://shop.pimoroni.com/products/5-vdc-stepper-motor-with-uln2003-driver-board)

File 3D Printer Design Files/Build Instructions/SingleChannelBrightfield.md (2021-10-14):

# Single Channel Brightfield Microscope

This section of the FreeCAD file includes designs where we have placed the individual cube designs together to create larger parts for 3D printing. These designs are specifically for parts for a single channel brightfield microscope. This microscope includes a low cost LED which can be controlled using the PiStep2 stepper motor hat for a Raspberry Pi, a finite conjugate objective and a Raspberry Pi v2 camera. If you wanted you could also swap the finite conjugate objective for an infinity corrected one and then add a tube lens between the objective and camera using on of our lens inserts.

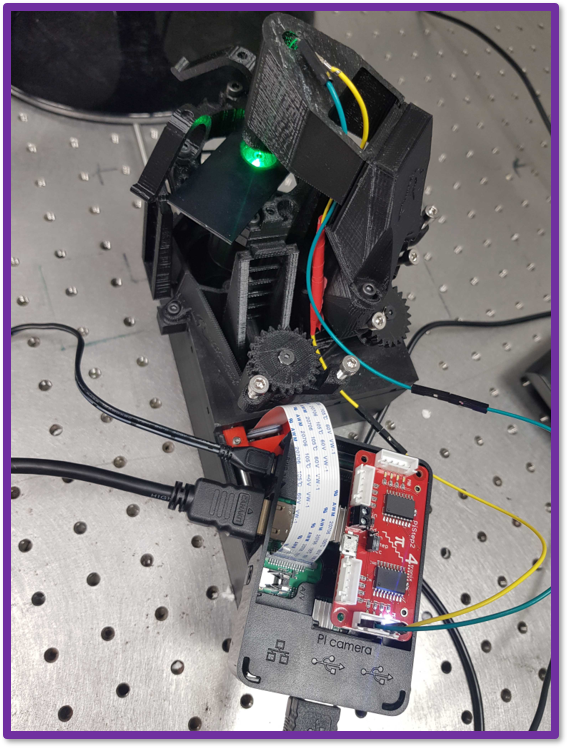
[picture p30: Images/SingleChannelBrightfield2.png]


The PiStep2 motor control board has 4 stepper motor connectors. On each of these connectors there is one ground pin and 4 pins which connect to the Raspberry Pi GPIO pins. As we only need to use three stepper motors for the OpenFlexure stage, there is one spare. This spare one can be used to connect to the LED to control it via GPIO. Using jumper cables connect the cathode of the LED to the ground pin on connector M1. The ground pin on the connector is the one which is not connected to an indicator LED. Then connect the anode to the pin on connector M1 which corresponds to GPIO pin 23 on the pi (This is the pin that I define in our control software [here](https://github.com/NanoBioPhotonics-Strathclyde/M4All/tree/main/Control%20Software/StepperMotorandLEDGUI)). You should also connect a suitable resistor between the anode and the connector pin. **Note: The photo above is of an older version. Please see the photo below for which pins to connect to. We have used JST XH connectors below but you can also use jumper cables as above.**

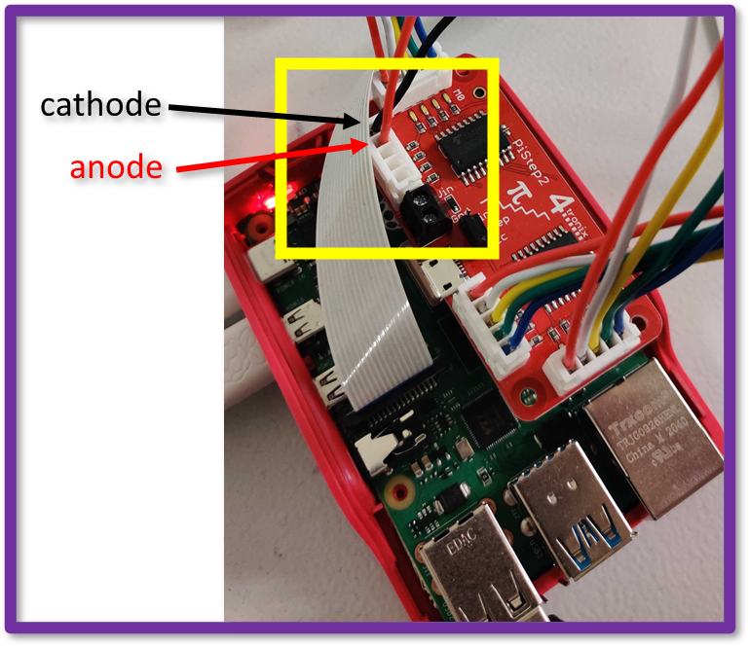
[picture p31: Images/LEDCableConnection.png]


## Parts to Print

All the STL files for this microscope can be found in [Single Channel Brightfield](https://github.com/NanoBioPhotonics-Strathclyde/M4All/tree/main/3D%20Printer%20Design%20Files/STL%20Files/Single%20Channel%20Brightfield).

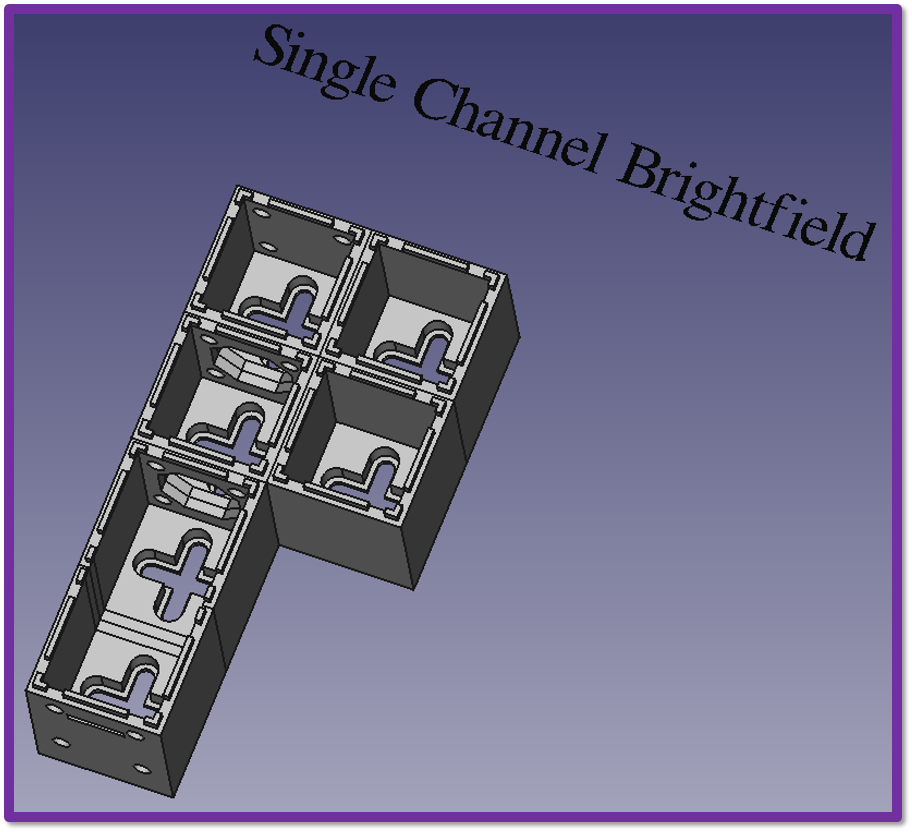
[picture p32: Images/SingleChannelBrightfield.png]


STL files to print (print settings can be found in the [Cubes](https://github.com/NanoBioPhotonics-Strathclyde/M4All/blob/main/3D%20Printer%20Design%20Files/Build%20Instructions/Cubes.md) and [Inserts](https://github.com/NanoBioPhotonics-Strathclyde/M4All/blob/main/3D%20Printer%20Design%20Files/Build%20Instructions/Inserts.md) build instructions):

* 1x Single Channel Brightfield
* 1x Single Channel Brightfield Lid
* 1x OpenFlexure Joined to Objective Mount
* 1x OpenFlexure Sample Riser Shortened
* 1x OpenFlexure Stage Adapter
* 1x Raspberry Pi Camera V2 Holder
* 1x 45 Degree Mirror Holder

Also from the OpenFlexure [website](https://microscope-stls.openflexure.org/#/v6.1.5?enable_smart_brim=true&reflection_illumination=false&optics=rms_f50d13&camera=picamera_2&use_pilens_optics_module=false&riser=sample&microscope_stand%3Abox_h=30&pi_in_base=true&base=bucket&legacy_picamera_tools=false&include_actuator_tension_band=false&include_actuator_drilling_jig=false&motorised=true&use_motor_gears_for_hand_actuation=false) please print the gears, small gears, sample clips, condenser and illumination dovetail STL files.

## Bill of Materials

* Light source:
  * Low cost LED
* Turning mirror:
  * 1x Thorlabs PF10-03-P01 - Ø1" Protected Silver Mirror (https://www.thorlabs.com/thorproduct.cfm?partnumber=PF10-03-P01)
* Camera:
  * 1x Raspberry Pi Camera Module v2 (https://www.raspberrypi.org/products/camera-module-v2/)
* Objective:
  * 1x Newport M-60X Microscope Objective Lens
* Cage rods:
  * 2x Thorlabs ER8 - Cage Assembly Rod, 8" Long, Ø6 mm (https://www.thorlabs.com/thorproduct.cfm?partnumber=ER8)
  * 2x Thorlabs ER6 - Cage Assembly Rod, 6" Long, Ø6 mm (https://www.thorlabs.com/thorproduct.cfm?partnumber=ER6)
  * An equivalent to the Thorlabs rods is to buy lower cost stainless steel 6mm diameter rods. For example we bought 1.5m long rods from RS Components and cut them down to size - https://uk.rs-online.com/web/p/metal-bars-metal-rods/6614680/
* Electronics:
  * 1x Raspberry Pi 4 8gb (Recommend a starter kit https://uk.rs-online.com/web/p/raspberry-pi/2012367)
  * Jumper cables (https://shop.pimoroni.com/products/jumper-jerky?variant=348491271)

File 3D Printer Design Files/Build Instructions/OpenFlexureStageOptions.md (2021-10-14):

# OpenFlexure Options

We needed to make a couple of modifications to the OpenFlexure stage for it to be compatible with our modular system. The first is the objective mount was too long and wouldn't allow a turning mirror to sit underneath the stage in one of our cubes, so we altered the objective mount to make it shorter. The second was we encountered problems with tilt of the objective mount when screwing it onto the stage, therefore we combined the designs for the stage and the objective mount to print them together monolithically. We think this wasn't a fault of the stage design but a fault in the calibration of our 3D printer, commonly known as "[elephant foot](https://all3dp.com/2/elephant-s-foot-3d-printing-problem-easy-fixes/)". By making these two parts monolithic we avoid the need to worry about this calibration error.

These parts were printed with the settings recommended by OpenFlexure (https://build.openflexure.org/openflexure-microscope/v6.1.5/docs/#/0_printing).

# Altered OpenFlexure RMS Objective Mount

We imported the STL file for the OpenFlexure Objective mount (named "optics_picamera_2_rms_f50d13.stl" from https://openflexure.org/projects/microscope/build) into FreeCAD and edited it following the instructions found here for editing STL files in FreeCAD - https://all3dp.com/1/7-free-stl-editors-edit-repair-stl-files/. All we did was cut the bottom of the mount off in FreeCAD to make it shorter.

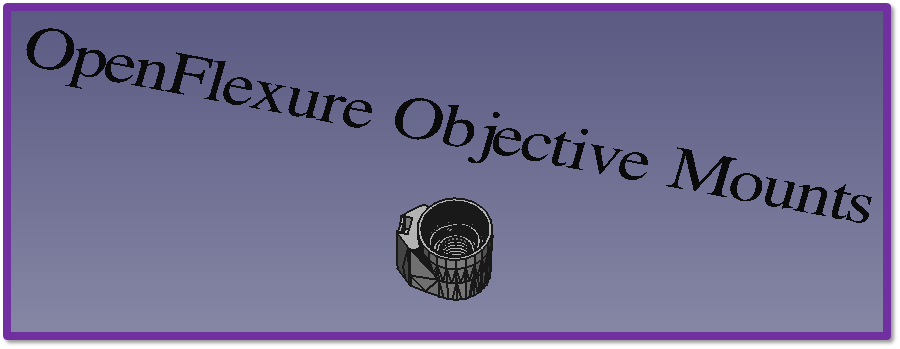
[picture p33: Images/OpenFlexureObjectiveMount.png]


# OpenFlexure Stage Option

To join the designs of the above objective mount together with the OpenFlexure Stage, we imported the STL file for the desired OpenFlexure stage into FreeCAD, then duplicated the objective mount design and moved it so that it was flush with the stage design. We added both these files to a "part" in FreeCAD and then exported the part as an STL file. We then also edited the OpenFlexure sample riser (named sample_riser_LS10.stl from https://openflexure.org/projects/microscope/build) using the same process as for the objective mount to shorten it for our specific objective. This is needed because the position of the objective mount is now fixed. The objective this is designed for is the Newport LI-60x (https://www.newport.com/p/LI-60X). This objective is no longer available however it has a standard parfocal length of 45mm and so this stage option should be compatible with other 45mm parfocal RMS threaded objectives. The parfocal length is normally specified by the manufacturer but for completeness it is defined as the distance from the mounting surface of the objective to the in-focus plane.

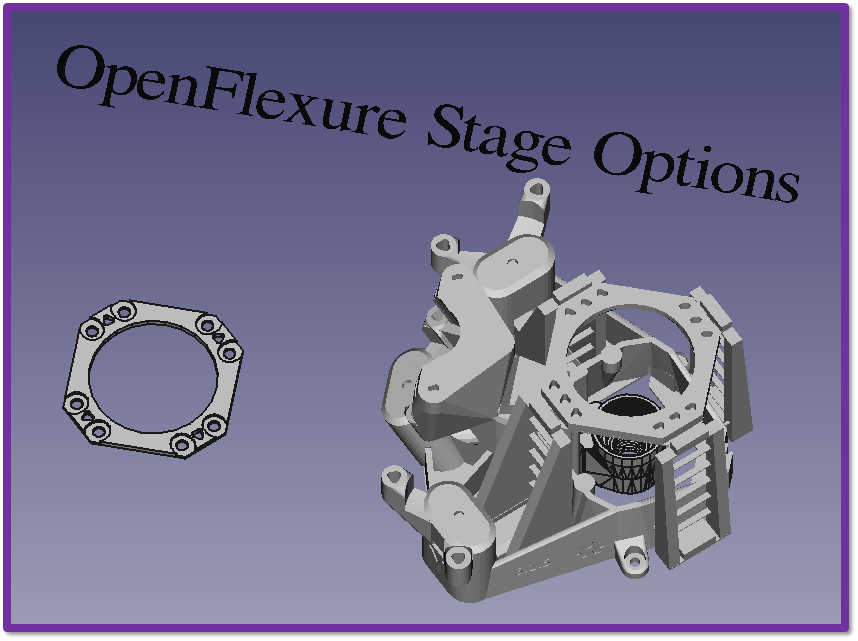
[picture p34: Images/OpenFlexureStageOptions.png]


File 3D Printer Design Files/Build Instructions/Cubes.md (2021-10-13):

# Cubes

The cubes and lids are all printed in the same orientation that they appear on FreeCAD, with the exception of the locking plates for the beamsplitter cubes - these will need to be reorientated in your 3D printing software such as Cura. We print the cubes and lids on our Ultimaker S5 with a layer height of 0.15mm and infill of 80% or more. In order to avoid needing to use support material for the cubes, I also enable bridge settings on Cura with the settings as shown below:

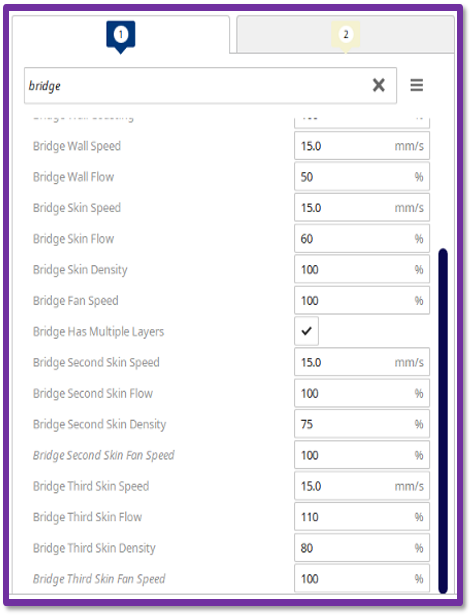
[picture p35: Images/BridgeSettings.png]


## Basic Cubes

The image below shows the various cube designs under "Basic Cubes". These are as follows:
  * The cube with no sides cut out can be used as a filler cube, for example if you need an extra cube to use with an attachment for another part or piece of equipment. For example we use one of these when using the adapter for the OpenFlexure microscope.
  * The cube with one side cut out can be used as an end cube in a system.
  * There are two different designs for cubes with two sides cut out. One has opposite walls cut out and can be used in the middle of an optical path. The other has adjacent sides cut out and can be used as a corner cube, for example to hold a turning mirror.
  * Then there is one with three walls and one with all four walls cut out to allow junctions between branches.
  * Finally we have provided one where the end wall has a slot for a raspberry pi camera cable. 

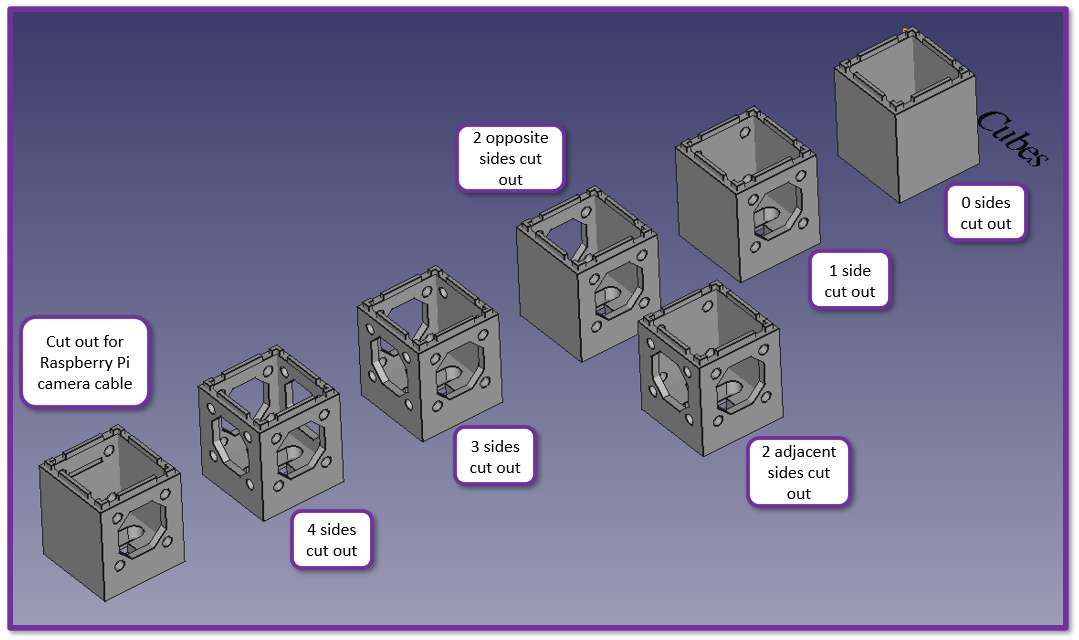
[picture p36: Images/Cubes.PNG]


## Open Ended Cubes

The next section is "Open Ended Cubes". These can be used in the case where you need a cube with a length larger than 50mm. For example if an optical element needs to sit where a wall would be positioned or if you need to be able to slide elements back and forth. There are two open ended cube designs:
  * The first has one side open ended. You can join two of these together to create a 100mm long cube.
  * The second has both sides open ended so if you require longer than 100mm then you can place as many of these in the middle of two single open ended cubes as required.

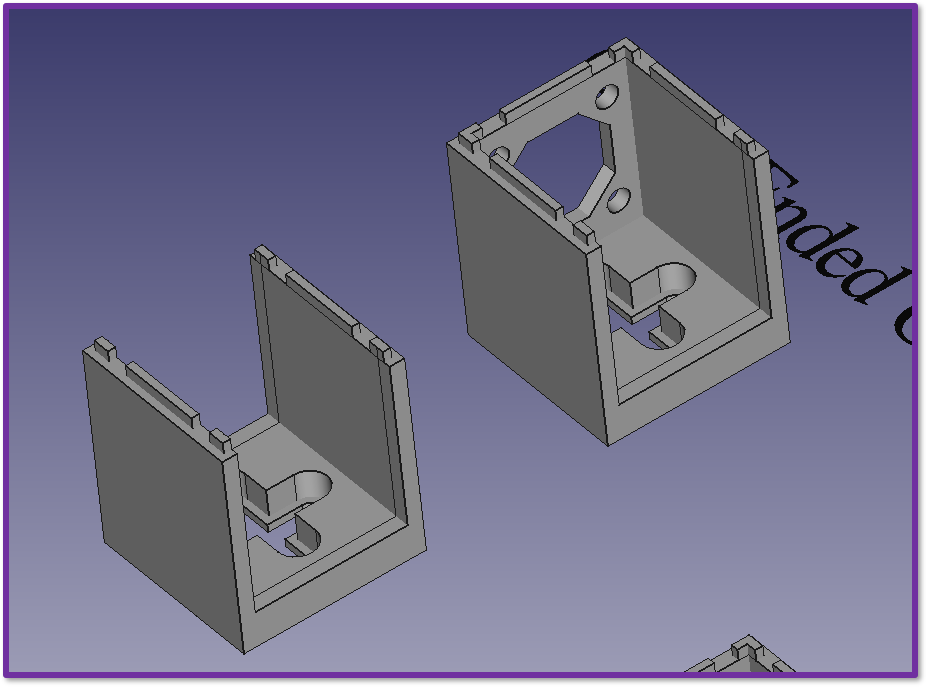
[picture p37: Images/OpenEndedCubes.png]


## 25mm x 36mm Beamsplitter Cubes
  
The third section of cubes is "25mm x 36mm Beamsplitter Cubes". As 25mm x 36mm rectangular optics are not compatible with the 30mm cage system we have designed three different cube options for holding this size of optics:

Note: The current designs are to hold a plate thickness of 1mm, but this can be altered in FreeCAD.

1. **Beamsplitter Cube** has a plate holder that is monolithically printed inside the cube. Two bars can then be screwed in place using M3 screws to hold the optic in place. As the screws need to be screwed in through the holes in the cube walls, this part is only suitable if printed as a single cube and not joined to others where these walls would be blocked.
2. **Beamsplitter Cube001** is similar to the first option, however this design includes a plate locker that slides into two gaps on the bottom of the cube and screws onto the top of the plate. Therefore this cube can be joined to others and printed monolithically.
3. **Beamsplitter Cube002** has the plate holder separate from the cube. The cube includes a section where the plate holder can be inserted into and the same bars as in the first option are included for holding the optic in place.

It is recommended to print these with either support material or if using Cura to enable bridge settings.

For option 2, if you find that your optical element is not sitting completely vertical (e.g. if there is an angle to the reflected and transmitted beams), you can add shims to the inside of the plate locker by adding layers of electrical tape to either the top or bottom.

Option 3 has not yet been fully tested.

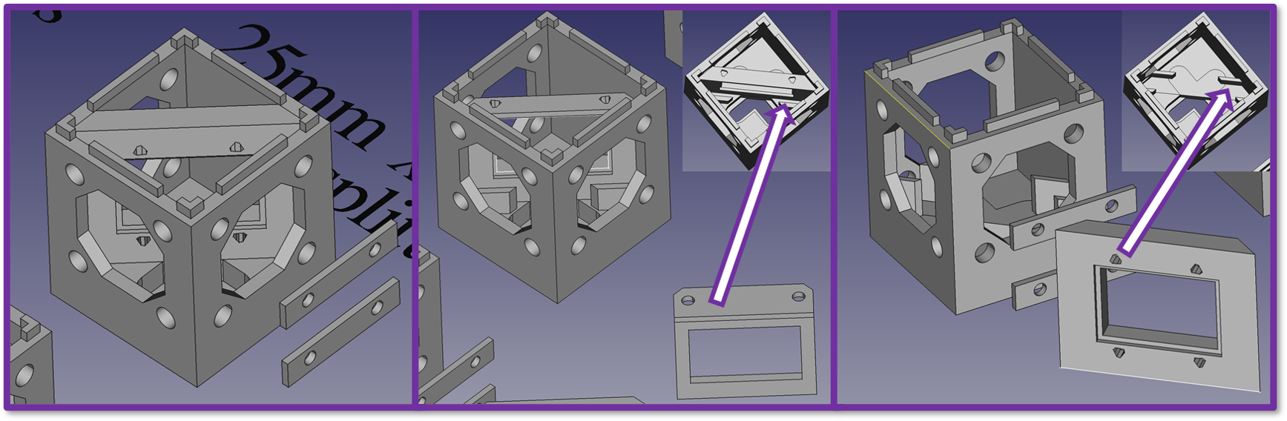
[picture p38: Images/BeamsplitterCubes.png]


## Cube Lids

There are two screwless lids that fix onto the top of the cubes using a jigsaw system to allow a light tight optical setup. One is a lid that covers one full cube. The other is half a lid (split diagonally) to cover half a cube. This second option is to fit with the second option OpenFlexure stage adapter (see build instructions). These lids can be joined together in FreeCAD to print monolithically to cover multiple cubes.

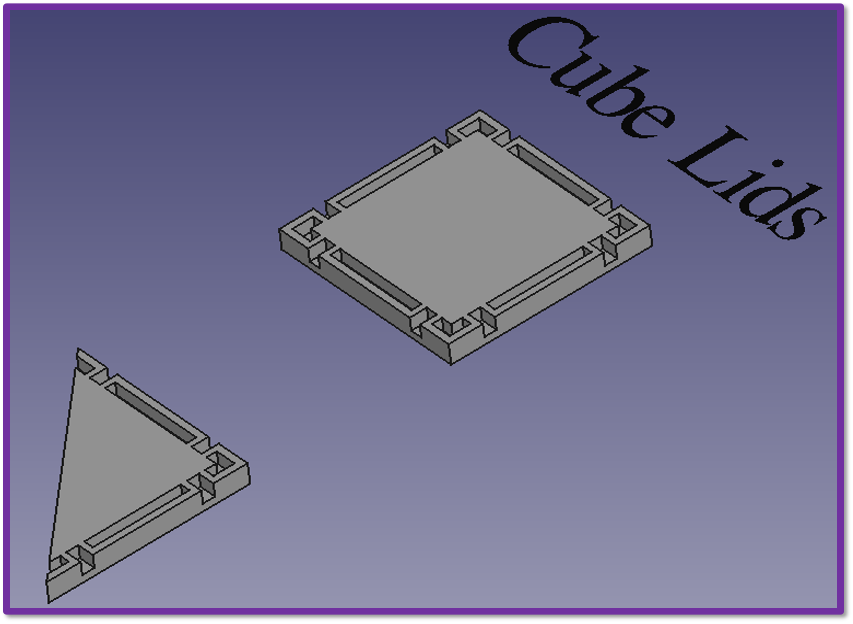
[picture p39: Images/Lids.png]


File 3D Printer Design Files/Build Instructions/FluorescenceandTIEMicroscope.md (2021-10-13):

# Fluorescence and TIE Microscope

This section of the FreeCAD file includes designs where we have placed the individual cube designs together to create larger parts for 3D printing. These designs are specifically for parts for a multimodal microscope which allows single channel fluorescence imaging and also computational phase imaging based on the transport of intensity equation (TIE). For more information on TIE microscopy please see these papers:

* https://arxiv.org/abs/1707.04139
* https://royalsocietypublishing.org/doi/10.1098/rsos.191921#d3e402

For TIE microscopy, you need to acquire three brightfield images at three different z planes in the sample. Ideally the three planes should be equally spaced apart in z. Our microscope (shown below), which allows TIE images to be acquired, has an infinity corrected objective lens allowing us to create multiple detection channels before focusing the light down onto various cameras. The first channel is a fluorescence channel where, in this case, we excite the sample (such as nanodiamonds) with a 532nm diode laser. Using a 650nm shortpass dichroic allows fluorescence emission above this wavelength to be picked off into the detection channel. The remaining transmitted laser light can then be utilised for TIE imaging. By splitting this light into three channels using beamsplitters, we can offset the tube lenses and focus on three different z planes simultaneously (note: postprocessing for both magnification and xy translation registration may be needed between the channels).



## Parts to Print

All the STL files needed for this microscope can be found in [Fluorescence and TIE Microscope](https://github.com/NanoBioPhotonics-Strathclyde/M4All/tree/main/3D%20Printer%20Design%20Files/STL%20Files/Fluorescence%20and%20TIE%20Microscope).

These are the two main cube parts:

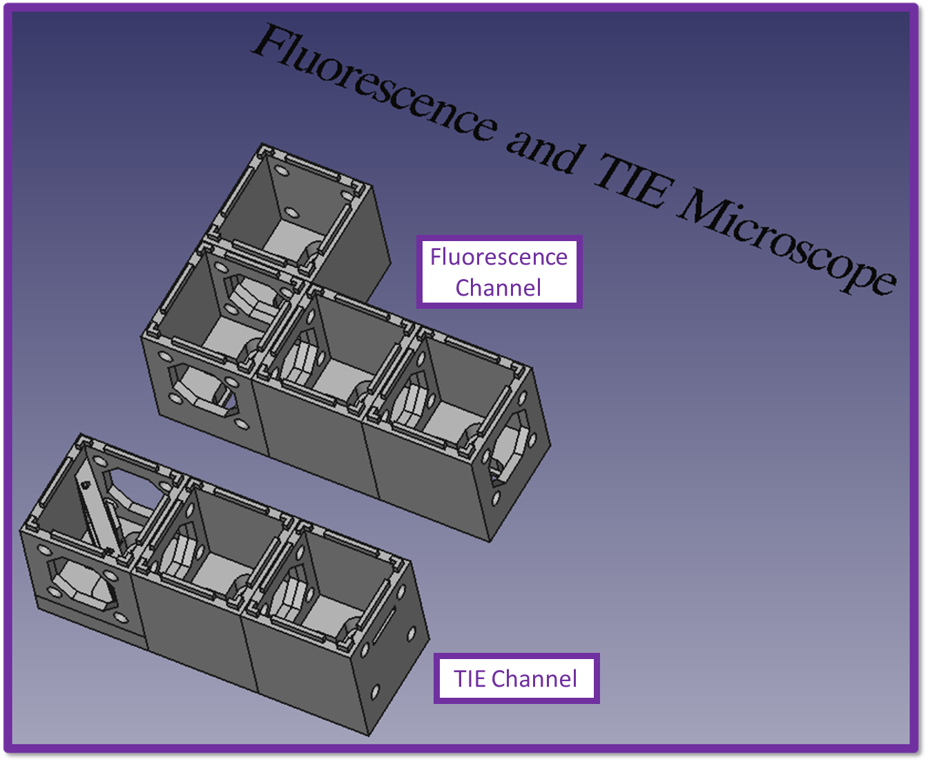
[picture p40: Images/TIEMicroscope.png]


STL files to print (print settings can be found in the [Cubes](https://github.com/NanoBioPhotonics-Strathclyde/M4All/blob/main/3D%20Printer%20Design%20Files/Build%20Instructions/Cubes.md) and [Inserts](https://github.com/NanoBioPhotonics-Strathclyde/M4All/blob/main/3D%20Printer%20Design%20Files/Build%20Instructions/Inserts.md) build instructions):

* 1x 1 Inch Dichroic Holder
* 4x 1 Inch Lens Holder
* 4x 1 Inch Retaining Ring
* 1x 45 Degree Mirror Holder
* 1x Dichroic Locker
* 4x Drop In Filter Holder
* 1 x Fluorescence Branch
* 1x Fluorescence Channel Lid
* 1x OpenFlexure Joined to Objective Mount
* 1x OpenFlexure Sample Riser Shortened
* 1x OpenFlexure Stage Adapter Corner Cut Out
* 3x Plate Locker
* 3x TIE Branch
* 3x TIE Channel Lid
* 3x Raspberry Pi Camera V2 Holder

Also from the OpenFlexure [website](https://microscope-stls.openflexure.org/#/v6.1.5?enable_smart_brim=true&reflection_illumination=false&optics=rms_f50d13&camera=picamera_2&use_pilens_optics_module=false&riser=sample&microscope_stand%3Abox_h=30&pi_in_base=true&base=bucket&legacy_picamera_tools=false&include_actuator_tension_band=false&include_actuator_drilling_jig=false&motorised=true&use_motor_gears_for_hand_actuation=false) please print the gears, small gears and sample clips STL files.

## Bill of Materials

* Light source:
  * 1x Thorlabs CPS532 Collimated Laser Diode (https://www.thorlabs.com/thorproduct.cfm?partnumber=CPS532)
  * Lens to focus laser down onto sample, such as Thorlabs LB1945-A - N-BK7 Bi-Convex Lens, Ø1", f = 200.0 mm, ARC: 350-700nm (https://www.thorlabs.com/thorproduct.cfm?partnumber=LB1945-A)
* Turning mirror:
  * 1x Thorlabs PF10-03-P01 - Ø1" Protected Silver Mirror (https://www.thorlabs.com/thorproduct.cfm?partnumber=PF10-03-P01)
* Dichroic Mirror for fluorescence channel:
  * 1x Thorlabs DMSP650 - Ø1" Shortpass Dichroic Mirror, 650 nm Cutoff (https://www.thorlabs.com/thorproduct.cfm?partnumber=DMSP650)
* Beamsplitters for brightfield TIE channels:
  * 1x Thorlabs BSS10R - 25 x 36 mm 30:70 (R:T) UVFS Plate Beamsplitter, Coating: 400 - 700 nm, t = 1 mm (https://www.thorlabs.com/thorproduct.cfm?partnumber=BSS10R)
  * 1x Thorlabs BSW10R - 25 x 36 mm 50:50 UVFS Plate Beamsplitter, Coating: 400 - 700 nm, t = 1 mm (https://www.thorlabs.com/thorproduct.cfm?partnumber=BSW10R)
* Second turning mirror:
  * 1x Thorlabs PFR10-P01 - 25 mm x 36 mm Protected Silver Mirror (https://www.thorlabs.com/thorproduct.cfm?partnumber=PFR10-P01)
* ND filters for brightfield TIE channels:
  * 3x Thorlabs ND30B - Unmounted Reflective Ø25 mm ND Filter, Optical Density: 3.0 (https://www.thorlabs.com/thorproduct.cfm?partnumber=ND30B)
* Longpass filter to clean up fluorescence channel:
  * 1x Thorlabs FEL0650 - Ø1" Longpass Filter, Cut-On Wavelength: 650 nm (https://www.thorlabs.com/thorproduct.cfm?partnumber=FEL0650)
* Tube lenses:
  * 1x Thorlabs AC254-125-A - f = 125 mm, Ø1" Achromatic Doublet, ARC: 400 - 700 nm (https://www.thorlabs.com/thorproduct.cfm?partnumber=AC254-125-A) - Tube lens for Fluorescence Channel
  * 3x Thorlabs AC254-045-A - f = 45 mm, Ø1" Achromatic Doublet, ARC: 400 - 700 nm (https://www.thorlabs.com/thorproduct.cfm?partnumber=AC254-045-A) - Tube lenses for brightfield TIE channels - Due to field distortion and vignetting that occurs when these are used in combination with the Newport LI-40x objective, we now recommend using a longer focal length for the tube lens, such as Thorlabs AC254-100-A - f = 100 mm, Ø1" Achromatic Doublet, ARC: 400 - 700 nm (https://www.thorlabs.com/thorproduct.cfm?partnumber=AC254-100-A)
* Cameras:
  * IDS UI-3060CP-M-GL Rev.2 (https://en.ids-imaging.com/store/ui-3060cp-rev-2.html) - Fluorescence channel
  * 3x Raspberry Pi Camera Module v2 (https://www.raspberrypi.org/products/camera-module-v2/) - TIE channels
* Objective:
  * 1x Newport LI-40x Microscope Objective Lens, Infinity Corrected, 40x, 0.65 NA, 0.36 mm WD (https://www.newport.com/p/LI-40X) - This objective has been discontinued, this is Newport's new equivalent: https://www.newport.com/p/LIO-40X
* Cage rods:
  * 10x Thorlabs ER4 - Cage Assembly Rod, 4" Long, Ø6 mm (https://www.thorlabs.com/thorproduct.cfm?partnumber=ER4)
  * 4x Thorlabs ER6 - Cage Assembly Rod, 6" Long, Ø6 mm (https://www.thorlabs.com/thorproduct.cfm?partnumber=ER6)
  * An equivalent to the Thorlabs rods is to buy lower cost stainless steel 6mm diameter rods. For example we bought 1.5m long rods from RS Components and cut them down to size - https://uk.rs-online.com/web/p/metal-bars-metal-rods/6614680/
* Electronics:
  * 4x Raspberry Pi Zero W (We recommend getting a starter kit, such as https://uk.rs-online.com/web/p/raspberry-pi/1812039/ so that everything you need is included)
  * 1x Raspberry Pi 4 8gb (Again recommend a starter kit https://uk.rs-online.com/web/p/raspberry-pi/2012367)
  * 3x Raspberry Pi Camera Cable - Raspberry Pi Zero edition (https://shop.pimoroni.com/products/camera-cable-raspberry-pi-zero-edition?variant=32092803891283)
  * 1x PiStep2 Quad Stepper Controller for Raspberry Pi (https://4tronix.co.uk/blog/?p=1309)
  * 3x 28BYJ-48 5V DC Stepper Motor (https://shop.pimoroni.com/products/5-vdc-stepper-motor-with-uln2003-driver-board)

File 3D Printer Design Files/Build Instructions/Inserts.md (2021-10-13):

# Inserts

The orientation of the inserts in FreeCAD are the recommended printing orientation, with the exception of the Dichroic Locker - this will need laid flat in your 3D printing software before printing. 

The only two that require to be printed with support material are the 45 Degree Mirror Holder and the 1 Inch Dichroic Holder. For the 45 Degree Mirror Holder you can either use PLA as the support material or specific support material like PVA. For the 1 Inch Dichroic Holder it needs to be dissolvable support material like PVA.

We print all the inserts on an Ultimaker S5 using 0.2mm layer height and 50% infill on Cura. You can increase the infill for increased strength and you can also reduce the layer height for greater accuracy. So far we have only printed these in standared Ultimaker PLA.

## 45 Degree Mirror Holder

This part holds a 1 inch mirror with thickness 6mm at 45 degrees. This can be hung from the cage system rods in two different orientations. The first orientation is to reflect a beam coming vertically down into cubes by 45 degrees so that it can travel horizontally around the cube system. This is useful for sample stages that sit above the cubes. The second orientation allows beams to be turned inside the cube system.

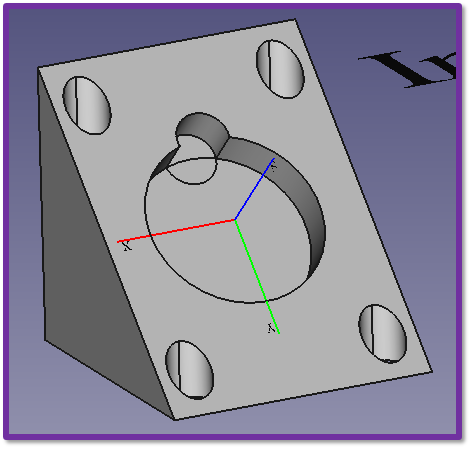
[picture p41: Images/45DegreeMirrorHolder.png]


The radius and thickness of the cylinder to hold the mirror can be altered in FreeCAD if different sized mirrors are required. Expanding the "Inserts" folder in the tree view on FreeCAD will then allow you to expand the body design "45 Degree Mirror Holder". Editing the "Mirror Hole" sketch will allow you to alter the radius. Editing the "Mirror Hole Pocket" will allow you to alter the thickness.

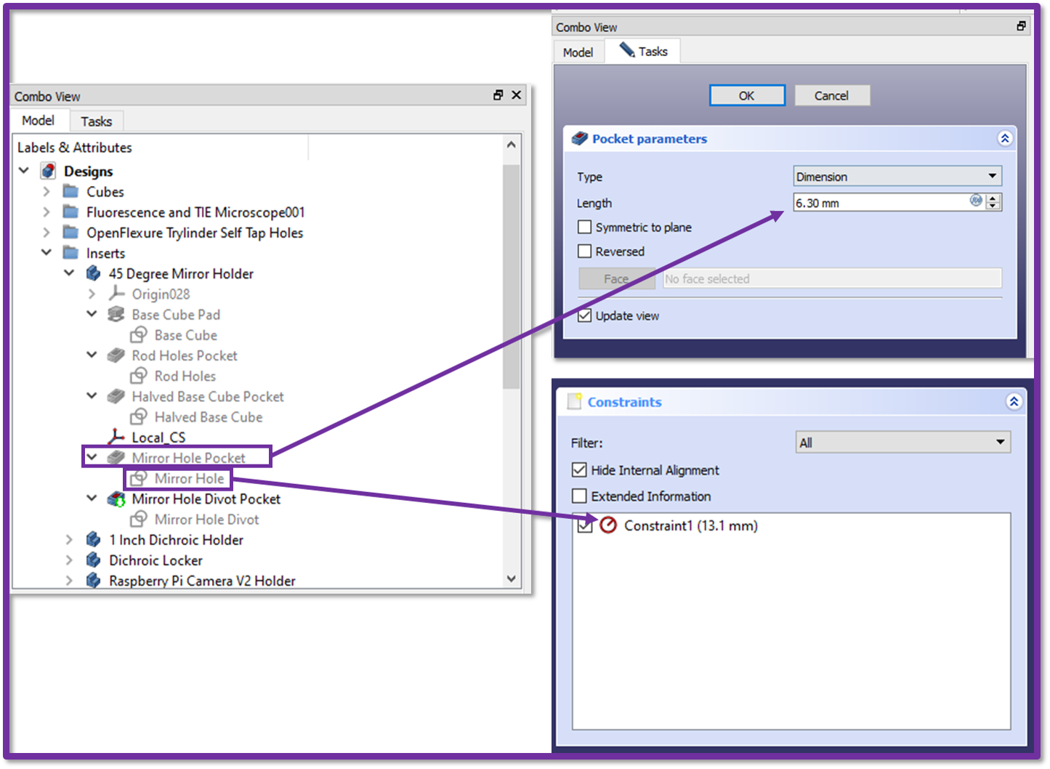
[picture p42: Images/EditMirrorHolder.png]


## 1 Inch Dichroic Holder

This part is similar to the mirror holder however it has channels to allow the transmitted beam to pass through the insert. It has been designed for a dichroic thickness of 3mm. There is also a plate to lock the dichroic in place with M3 screws. This part can also be used for 1 inch beamsplitters.

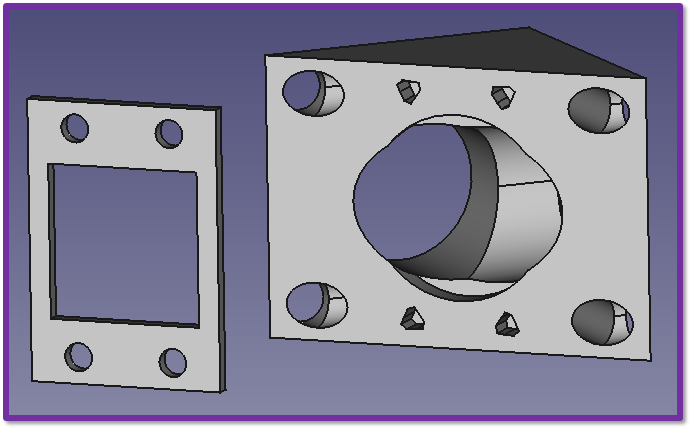
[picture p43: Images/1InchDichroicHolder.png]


Again the dimensions of the part can be altered in FreeCAD if different sized optics are required in the same way as above.

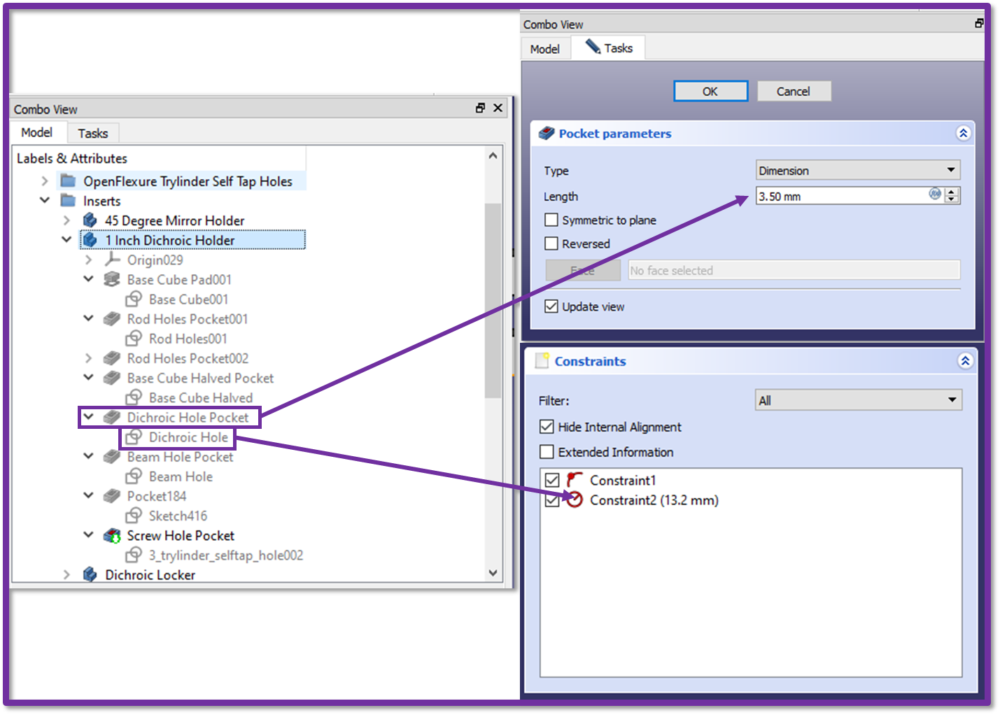
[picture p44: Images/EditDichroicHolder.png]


## Raspberry Pi Camera v2 Holder

This part has a slight indent for the camera module to fit into with a gap at the back for space for the electronics. There are 4 screw holes to hold the camera module in place with nuts at the back. The insert also has a cut out at the top for the camera cable. On the top of the insert there are self tapping M3 screw holes to provide some friction between the insert and the rods to hold it in place.

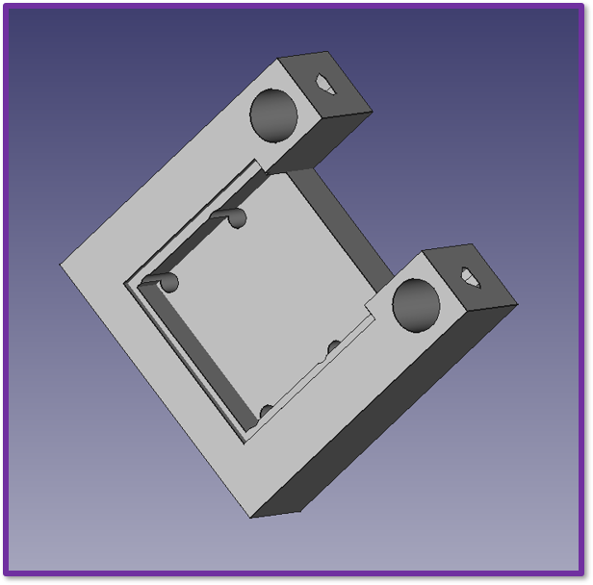
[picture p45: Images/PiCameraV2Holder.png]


## 1 Inch Lens Holder

This part is designed to hold a 1 inch lens or filter which can be held in place with the retaining ring design. The top of the insert again has M3 screw holes to hold the insert in place on the metal rods. 

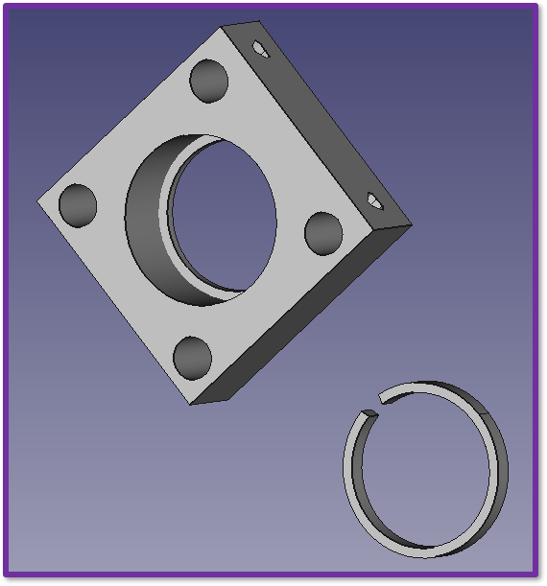
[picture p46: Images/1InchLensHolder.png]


If a greater thickness is required to hold thicker optics the FreeCAD design can be modified by increasing the "Base Square Pad" value as shown below. You can also make this smaller as well. Only changing this value should keep the thickness of the lip the same for holding the lens in place.

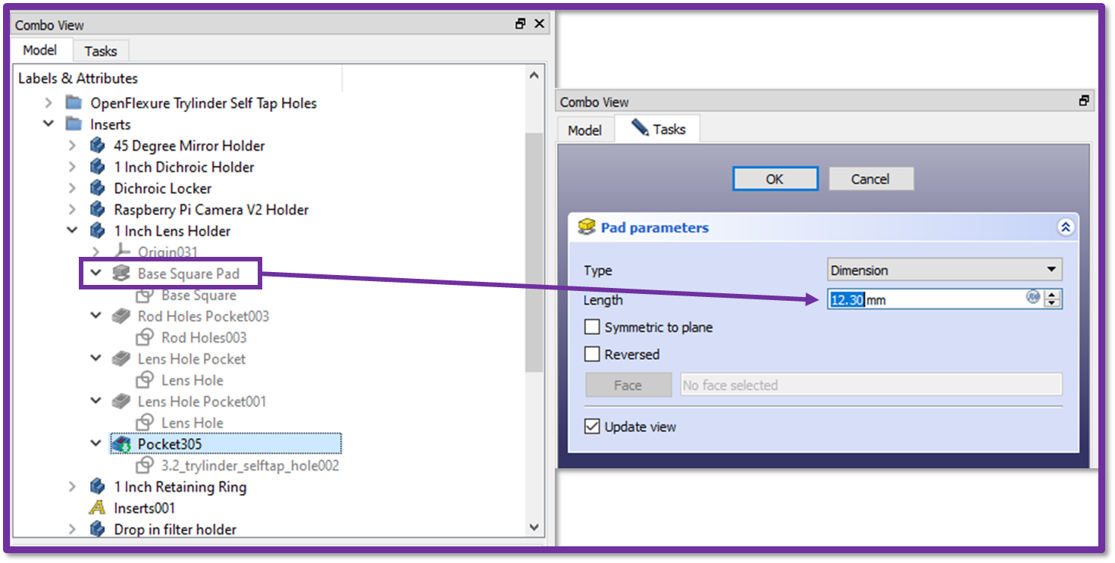
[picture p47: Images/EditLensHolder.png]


## Drop in Filter Holder

This part is designed to hold a 1 inch filter and can be easily dropped on and off the metal rods if you don't want it to be permanently in place so that nothing else in the system needs to be moved if you want to take it in and out. Again the 1 inch retaining ring can be used to hold the filter in place. Note: You can again increase the "Base Square Pad", however if the filter holder is too thick you won't be able to drop it in between the cage rods. This current thickness works, however I have not yet confirmed the limit on this thickness.

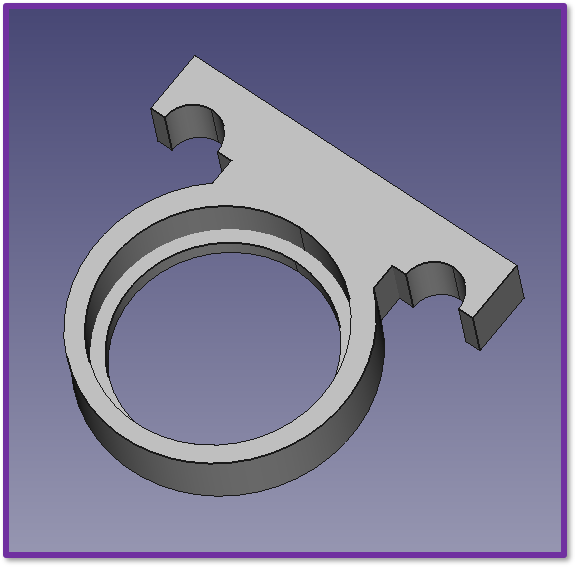
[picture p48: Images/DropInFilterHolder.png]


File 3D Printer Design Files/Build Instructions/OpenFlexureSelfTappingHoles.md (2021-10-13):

# OpenFlexure Self Tapping Holes

The Bath Open INstrumentation Group designed a test piece with varying sizes of self tapping trylinder holes (https://gist.github.com/rwb27/9c3ac259831a2d4316a7ae65a9f460fc). These are used on the OpenFlexure microscope for attaching the stepper motors to the actuators. We thought these were very useful and so used the STL file for the test piece to extract FreeCAD sketches of each of the hole sizes. We have used these sketches to create self tapping holes on a number of our designs.

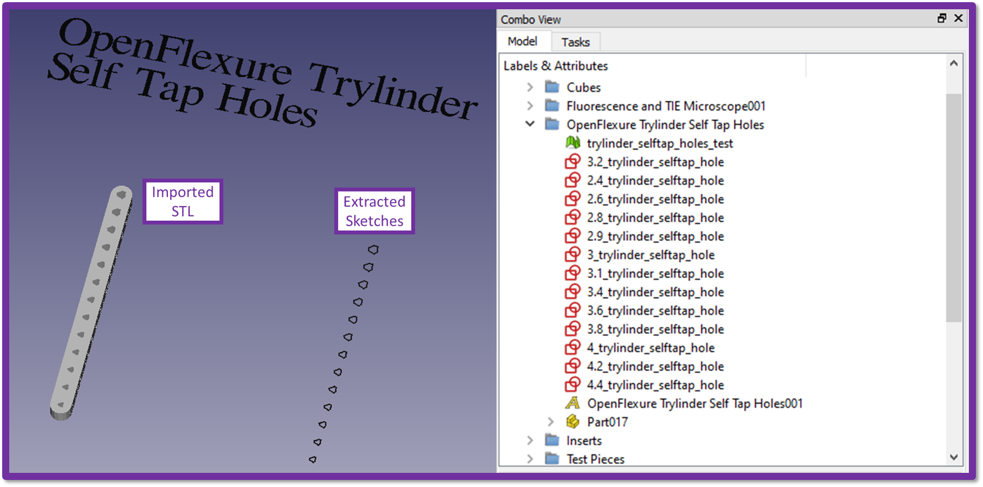
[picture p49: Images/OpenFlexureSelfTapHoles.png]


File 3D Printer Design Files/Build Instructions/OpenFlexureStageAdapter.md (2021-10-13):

# OpenFlexure Stage Adapter

The OpenFlexure stage is a 3D printable 3 axis control microscope stage (https://openflexure.org/projects/microscope/) developed by the Bath Open INstrumentation Group. In order to make this stage compatible with our modular cube system, we have developed an adapter that lets the stage attach to our cubes through the jigsaw lid system. This adapter also replaces the "feet" on the OpenFlexure Stage by providing a bar for each axis which the elastic band can wrap around instead of the standard feet, which allows a flush fit to our cubes.

We print this with 0.15mm layer height and 80% and higher infill. Support material is also required for the elastic band bars, this can either be standard PLA or PVA. It is best to print this piece with the jigsaw system facing up.

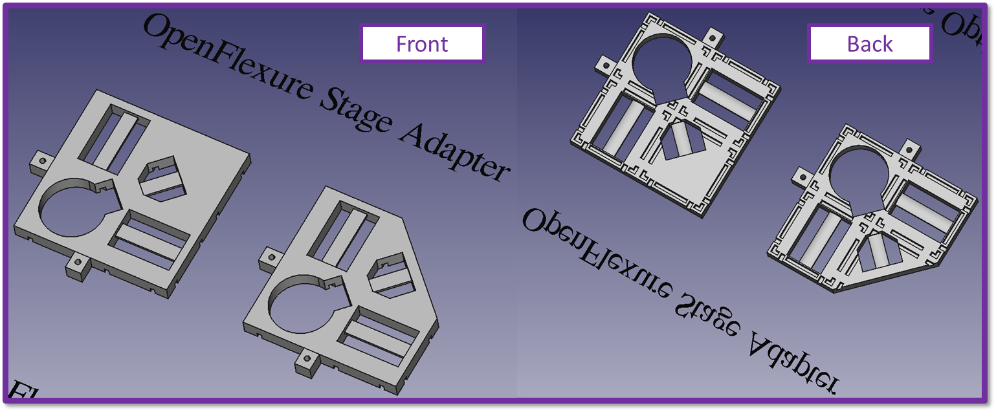
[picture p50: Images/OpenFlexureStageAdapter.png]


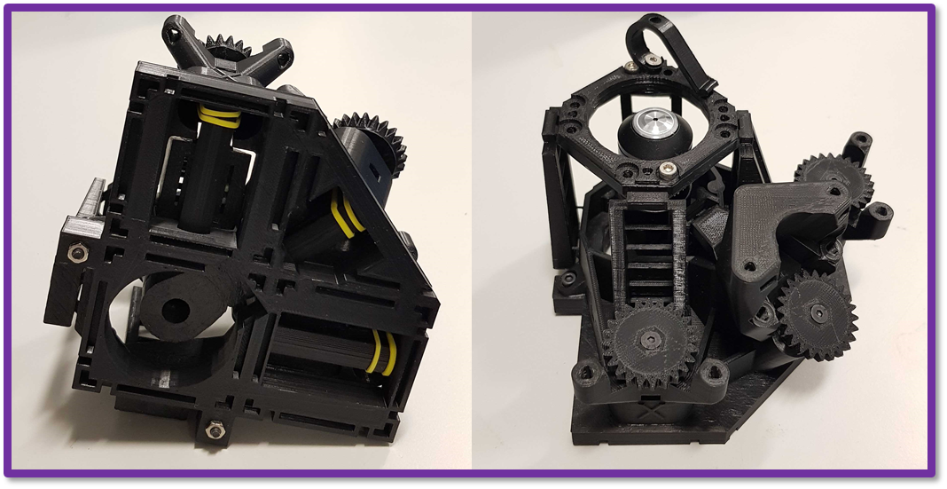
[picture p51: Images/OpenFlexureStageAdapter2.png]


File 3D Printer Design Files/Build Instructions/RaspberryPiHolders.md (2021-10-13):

# Raspberry Pi Holders

These are 3D printed cases for Raspberry Pi's which can be screwed down onto an optical bench or other surface to stop them moving about. So far I have only designed one to hold three Raspberry Pi Zero W's to be used with a three channel system where three Raspberry Pi Cameras are required. This can be printed with 0.2mm layer height and 50% or greater infill.

## Raspberry Pi Zero Case and Base

The case and base for three Raspberry Pi Zero W's are shown below. The case part has all the cut outs needed to access all the ports on the Pi. The base has two rectangular cut outs to allow it to be secured to an optical bench with M6 screws. The case attaches to the base through a jigsaw system. If there is tension on the Raspberry Pi cables, the parts may pop out from one another and so a crude solution is to tape the case to the base. This case should prevent the Pi's being damaged from any static electricity.

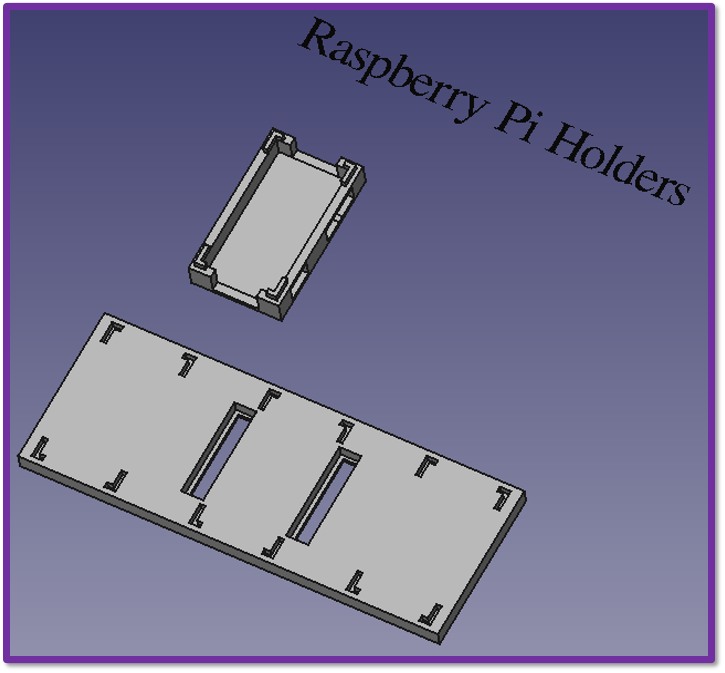
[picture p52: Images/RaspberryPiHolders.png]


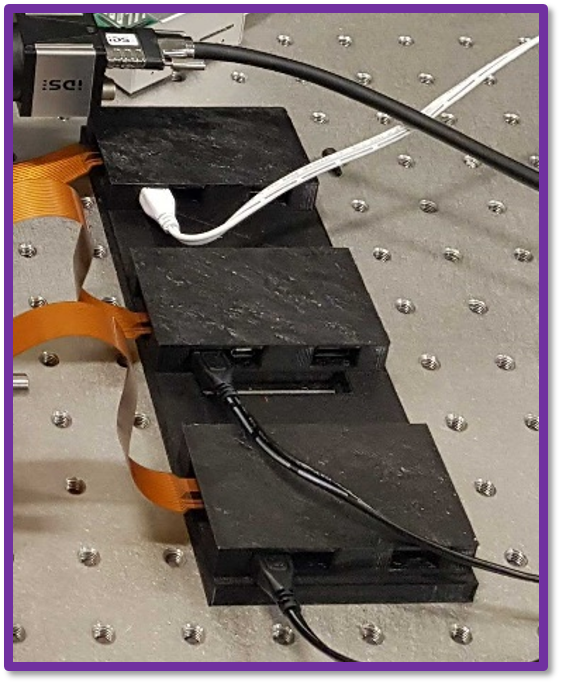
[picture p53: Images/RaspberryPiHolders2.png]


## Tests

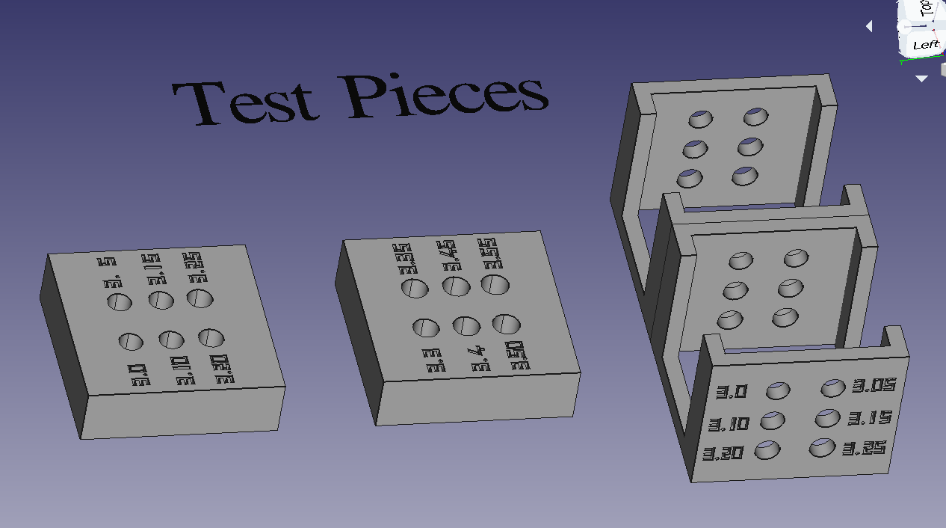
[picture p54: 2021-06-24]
3D Printer Design Files/Instruction Clips/Test Pieces.PNG

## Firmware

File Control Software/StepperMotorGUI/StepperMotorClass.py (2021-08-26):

#stepper motor class

import time
import sys
from threading import Thread
import RPi.GPIO as GPIO

class StepperMotor():
    def __init__(self):
        
        #Use BCM GPIO references
        GPIO.setmode(GPIO.BCM)

        #Define GPIO signals to use

        self.M0Pins = [17,18,27,22]
        self.M1Pins = [4,25,24,23]
        self.M2Pins = [13,12,6,5]
        #M3Pins = [20,26,16,19]

        #Set all pins as output
        for pin in self.M0Pins:
            GPIO.setup(pin,GPIO.OUT)
            GPIO.output(pin, 0)

        for pin in self.M1Pins:
            GPIO.setup(pin,GPIO.OUT)
            GPIO.output(pin, 0)

        for pin in self.M2Pins:
            GPIO.setup(pin,GPIO.OUT)
            GPIO.output(pin, 0)

        #for pin in M3Pins:
            #GPIO.setup(pin,GPIO.OUT)
            #GPIO.output(pin, 0)   

        #Define step sequence
        self.seq = [[1,0,0,0],
               [1,1,0,0],
               [0,1,0,0],
               [0,1,1,0],
               [0,0,1,0],
               [0,0,1,1],
               [0,0,0,1],
               [1,0,0,1]]
        
        #Define reversed step sequence
        self.seqreversed = [[1,0,0,1],
                       [0,0,0,1],
                       [0,0,1,1],
                       [0,0,1,0],
                       [0,1,1,0],
                       [0,1,0,0],
                       [1,1,0,0],
                       [1,0,0,0]]
        
        self.steps = 50
        
    def ChangeStepsPerClick(self,steps):
        self.steps = steps
        return self
    
    def XMoveLeftStart(self):
        self.xlstopped = False
        xl = Thread(target=self.XMoveLeft, args=())
        xl.daemon = True
        xl.start()
        return self        
    
    def XMoveLeft(self):       
        if self.xlstopped:
            return      
        for i in range (self.steps):
            for halfstep in range(8):
                for pin in range(4):
                    GPIO.output(self.M0Pins[pin], self.seq[halfstep][pin])
                    time.sleep(0.001)
        for pin in self.M0Pins:
            GPIO.output(pin, 0)
        self.xlstopped = True
        
    def XMoveRightStart(self):
        self.xrstopped = False
        xr = Thread(target=self.XMoveRight, args=())
        xr.daemon = True
        xr.start()
        return self 
        
    def XMoveRight(self):      
        if self.xrstopped:
            return
        for i in range (self.steps):
            for halfstep in range(8):
                for pin in range(4):
                    GPIO.output(self.M0Pins[pin], self.seqreversed[halfstep][pin])
                    time.sleep(0.001)
        for pin in self.M0Pins:
            GPIO.output(pin, 0)
        self.xrstopped = True
        
    def YMoveUpStart(self):
        self.yustopped = False
        yu = Thread(target=self.YMoveUp, args=())
        yu.daemon = True
        yu.start()
        return self

    def YMoveUp(self):        
        if self.yustopped:
            return
        for i in range (self.steps):
            for halfstep in range(8):
                for pin in range(4):
                    GPIO.output(self.M2Pins[pin], self.seq[halfstep][pin])
                    time.sleep(0.001)
        for pin in self.M2Pins:
            GPIO.output(pin, 0)
        self.yustopped = True
        
    def YMoveDownStart(self):
        self.ydstopped = False
        yd = Thread(target=self.YMoveDown, args=())
        yd.daemon = True
        yd.start()
        return self
        
    def YMoveDown(self):        
        if self.ydstopped:
            return
        for i in range (self.steps):
            for halfstep in range(8):
                for pin in range(4):
                    GPIO.output(self.M2Pins[pin], self.seqreversed[halfstep][pin])
                    time.sleep(0.001)
        for pin in self.M2Pins:
            GPIO.output(pin, 0)
        self.ydstopped = True
        
    def ZMoveUpStart(self):
        self.zustopped = False
        zu = Thread(target=self.ZMoveUp, args=())
        zu.daemon = True
        zu.start()
        return self
        
    def ZMoveUp(self):
        if self.zustopped:
            return
        for i in range (self.steps):
            for halfstep in range(8):
                for pin in range(4):
                    GPIO.output(self.M1Pins[pin], self.seq[halfstep][pin])
                    time.sleep(0.001)
        for pin in self.M1Pins:
            GPIO.output(pin, 0)
        self.zustopped = True
        
    def ZMoveDownStart(self):
        self.zdstopped = False
        zd = Thread(target=self.ZMoveDown, args=())
        zd.daemon = True
        zd.start()
        return self
        
    def ZMoveDown(self):
        if self.zdstopped:
            return
        for i in range (self.steps):
            for halfstep in range(8):
                for pin in range(4):
                    GPIO.output(self.M1Pins[pin], self.seqreversed[halfstep][pin])
                    time.sleep(0.001)
        for pin in self.M1Pins:
            GPIO.output(pin, 0)
        self.zdstopped = True

                

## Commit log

2021-06-24 Created 3D Printer Design Files Folder
    [1 Inch Dichroic Holder.stl, 1 Inch Lens Holder.stl, 1 Inch Retaining Ring.stl, 1x1 Cube Lid.stl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]
2021-06-24 Update and rename 3D Printer Design Files/Build Instructions/Basic Cubes.md to 3D Printer Design Files/Build Instruction/Cubes.md
2021-08-13 Added insert images
2021-08-25 Updated FreeCAD file and STL files
    [Drop In Filter Holder 2.stl, Drop In Filter Holder 3.stl, Drop In Filter Holder.stl, Fluorescence Channel Lid.stl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]
2021-08-25 Added STL files
    [Channel 1.stl, Fluorescence Branch.stl, OpenFlexure Joined to Objective Mount.stl, OpenFlexure Sample Riser Shortened.stl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]
2021-08-25 Create Plate Locker.stl
    [Plate Locker.stl]
2021-08-26 Added Stepper Motor GUI
2021-08-26 Added stepper motor and LED GUI
2021-10-13 Added single channel brightfield stl files
    [45 Degree Mirror Holder.stl, OpenFlexure Joined to Objective Mount.stl, OpenFlexure Sample Riser Shortened.stl, Openflexure Stage Adapter.stl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]
